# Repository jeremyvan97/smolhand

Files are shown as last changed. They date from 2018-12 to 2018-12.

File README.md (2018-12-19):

# The Smol Hand 1.0
## Introduction
The Purpose of this project is to create a decently-sized prosthetic arm, fit for a small child to use. Fit with EMG sensors, it allows the user to move the arm by twitching certain muscles, making it extremely easy to use.
This documentation goes through the design process, philosophy and schematics of the arm. For a quick look at the arm, check out this [video](https://www.youtube.com/watch?v=ZSc14HTJgZQ), which somewhat highlights the features of the arm (or at least an old version of it).

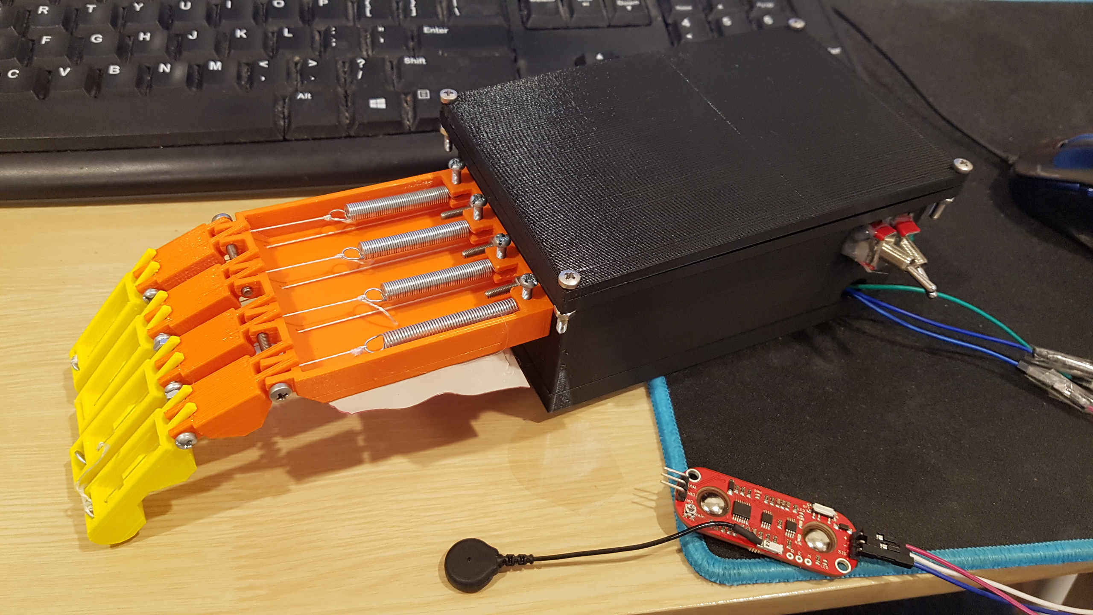
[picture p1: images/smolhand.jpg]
Smol hand


Before, we go any further, I would like to thank Yotaro Iwai, Williams Kwan and Jen Wen for being great teammates and making this a fun task.

## Disclaimer
This project was a semester-long assessment of the subject MCEN30019 Mechatronics Systems Design at the University of Melbourne. If you are currently enrolled in this subject, I **STRONGLY** advise you to design your own arm, not just because of plagiarism, but because it is more enjoyable and more knowledgeable to design one yourself (trust me).

## Let's get started

This project can be split into 3 main parts:
* Mechanical System
* Electrical System
* Software and Sensor

The gist of how the whole system works is that the sensor will read electric pulses from the user, which its readings will be then passed into a microcontroller (in this case it is an Arduino Nano). The microcontroller will then pass signals to the electrical system, which powers the actuator (a servo motor) and hence moves the mechanisms in the hand.

Throughout the project, we had decided to make the arm as simple and small as possible to accommodate for our target audience, a 10 year old child in a third world country.
>Any idiot can make something complicated. It takes good design to make something simple.
>
>-Rachel Macfarlane (quoted from somewhere else I think), 2018

## Mechanics
The mechanics behind the hand is rather simple. Each finger has two strings anchored in its top side and bottom side. The top string is connected to the palm, which is fixed. Between the palm and the string is a spring that pulls the finger back into the rest position when the servo is off.  
The bottom string is connected to the servo. When the servo is on, it pulls the finger downwards as the string creates a moment around the joints of the finger, making it curl inwards. There is a spring between the servo and the string to prevent damaging the rigid body of the arm when grabbing large objects.

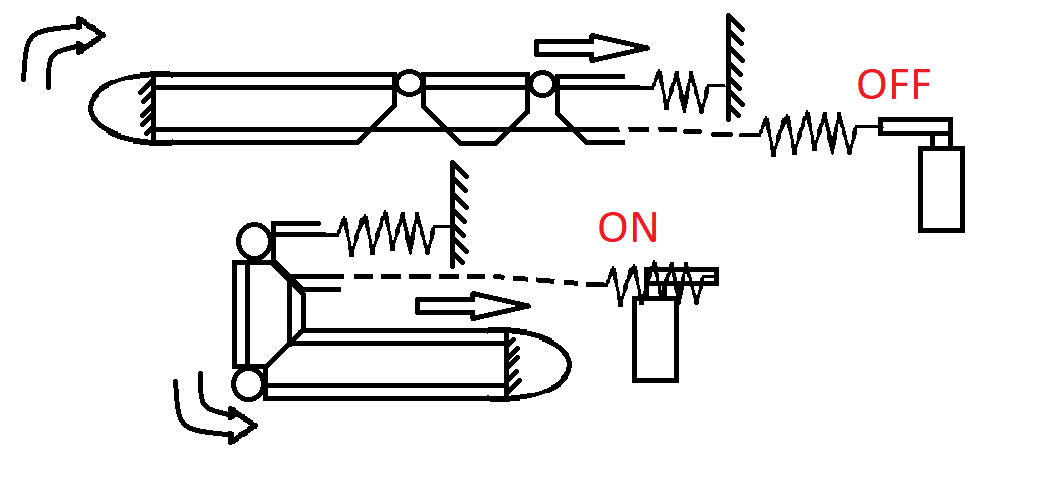
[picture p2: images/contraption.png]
Mechanics behind the fingers


We have designed these fingers to all be attached to the one same servo. This means that we **cannot** move the fingers individually. The reason we have done this is because we want to make the arm as small and light as possible for the child.

We have also decided not to give it a thumb as it might need it's own actuator, which requires more space and power. We have also found out after a bit of prototyping and experimenting that a thumb would hinder the efficiency of out design.

The parts and assembly of the arm are available in the repository for 3d printing (the .stl files must be scaled by 10x). The parts were designed in a way such that they are easy to assemble and all that is needed are M3 nuts and bolts. The finger parts have an extended end to prevent over-arching when returning to rest position. The top string goes above the bolt to create an upward moment.

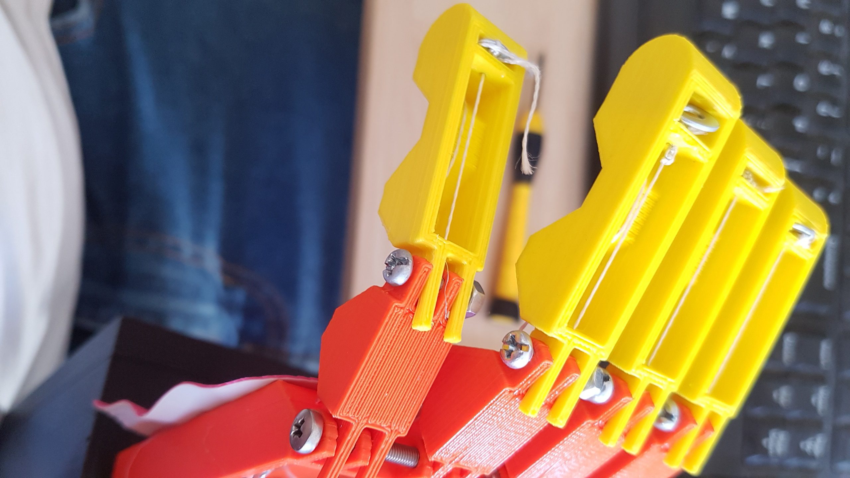
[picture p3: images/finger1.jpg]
Finger

>WD40 will always be your bestfriend.
>
>-Ethan Gan, 2018.

## Electrical
The electrical part of the arm consists of 2 switches and 2 power supplies. One of these switch-supply pairs powers the microcontroller, and the other powers the servo motor.  
A standard 9V battery is used to power the microcontroller, while the servo uses two 3.7V Li-ion batteries.

The microcontroller is connected to the EMG sensor and the servo motor. The connections for the circuit is shown below.

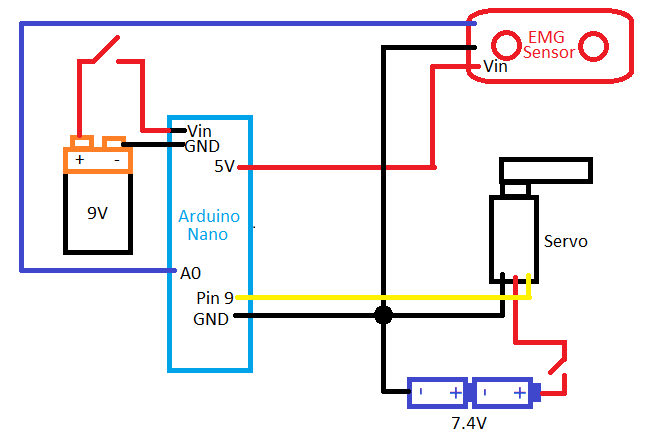
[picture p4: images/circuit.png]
Circuit


The EMG sensor reads the electrical pulses in your muscles. These readings are read by the microcontroller as a voltage depending on how strong of a pulse is given.
The microcontroller then sends a PWM signal to the servo depending on the readings read by the microcontroller.  
Here are the links to the [EMG sensors](https://www.sparkfun.com/products/13723) and [Servo motor](https://www.jaycar.com.au/servo-motor-standard-6-volt-with-metal-gear-11kg/p/YM2765) used (you could use any servo to your liking as long as you adjust the space allowed in the forearm).

A potential improvement for this circuit is to use a voltage regulator, which removes the need on a second power supply and relieving space.

## Software
The software basically makes the arm act as a finite state machine that only has 2 states: open and close. The controller only reacts when the reading is above a certain threshold (an electric pulse/muscle contraction), which then changes the state of the arm.

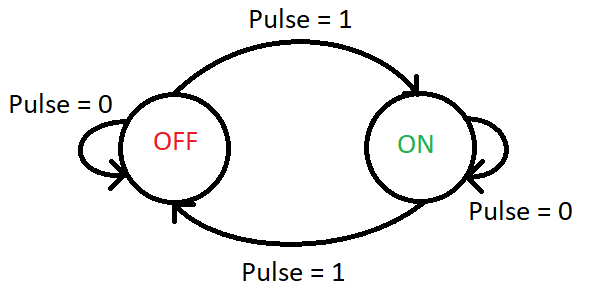
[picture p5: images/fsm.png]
Finite state machine


A possible improvement would be to implement a PID control to move the fingers at a wanted degree change instead of opening and closing entirely, though that would take a lot of time to test and calibrate.

## Assembly
The assembly should take about 2 hours. Each of the finger tips has to be connected to a joint, which is then attached to the palm.

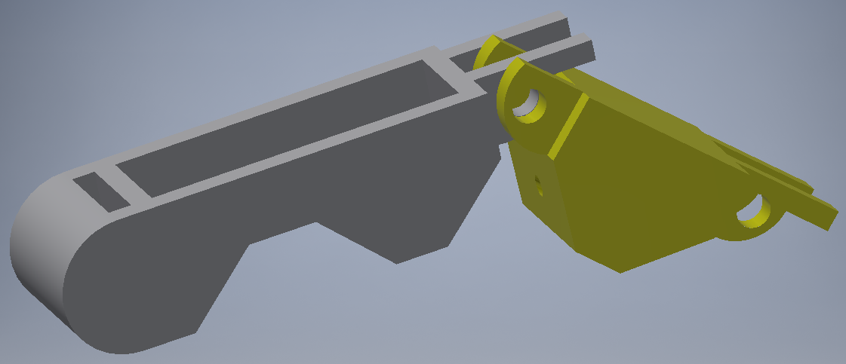
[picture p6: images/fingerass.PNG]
finger joints


Each finger should be given upper and lower strings (fishing line is what we used). Run the strings through its respective holes through the finger and the joint. Be sure that the upper string is above the bolt when assembling fingers. Once all the fingers have been assembled, run the strings into its respective holes into the palm. The palm is then attached to the forearm, which will house the electrical circuit.

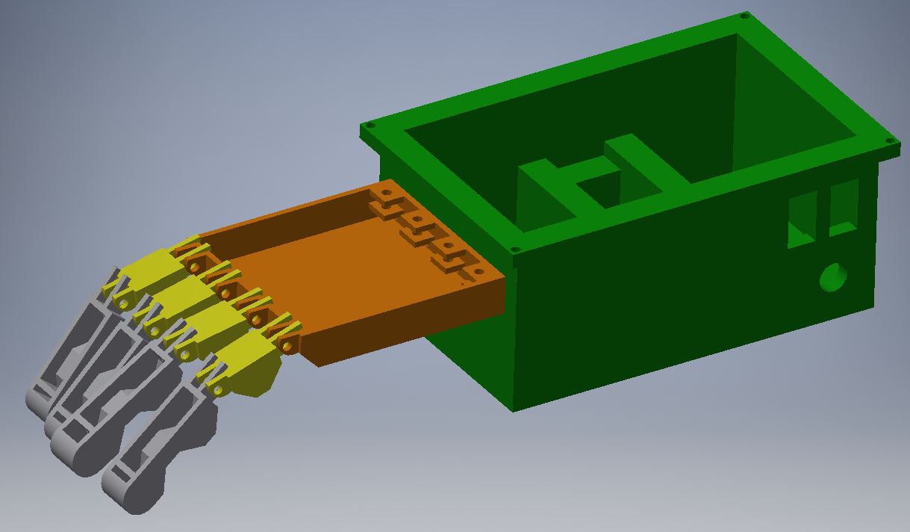
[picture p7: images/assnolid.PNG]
hand assembly


Connect the upper string to a spring each and lock them into the arm. Set up the forearm by placing the electrical components in the spaces shown below. Connect the lower strings and the servo via springs.
Sit the switches and wires through its allocated holes.

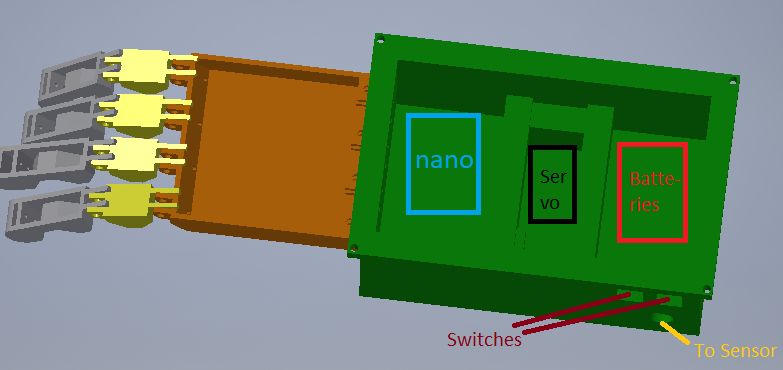
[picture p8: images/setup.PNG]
hand assembly 2


Once you have completed the assembly, it should look somewhat like this:

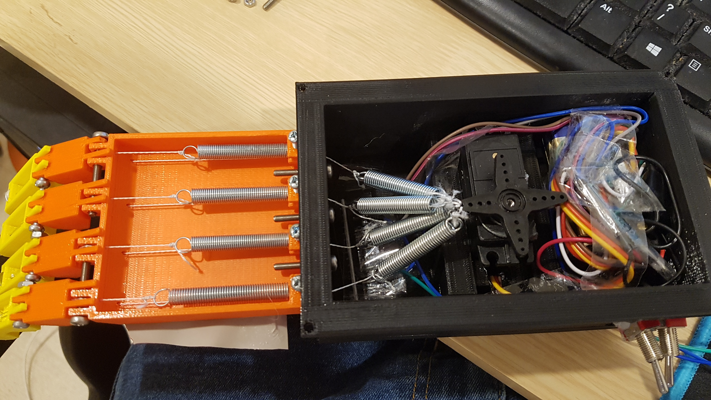
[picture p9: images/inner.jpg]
hand_irl


## Usage
Attach ECG electrodes onto the EMG sensor, then attach the electrodes to the back of your forearm (make sure the black electrode is as close to the bone as possible). Turn the switches on, and start moving your ring finger.

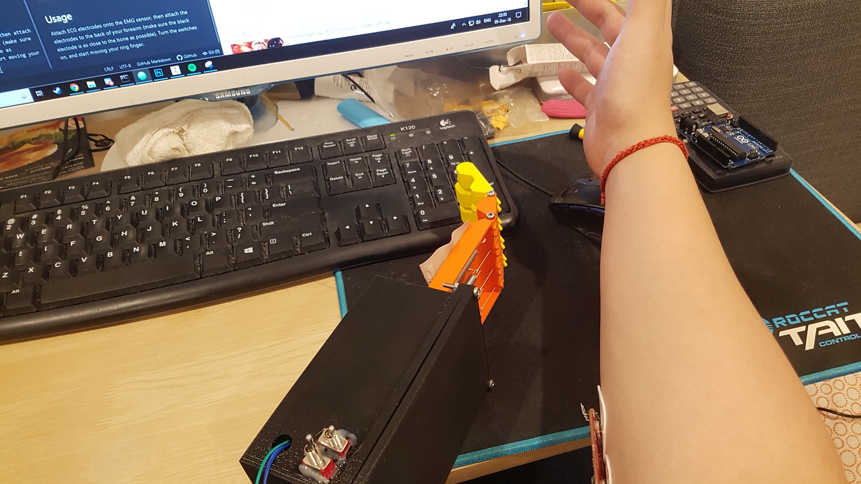
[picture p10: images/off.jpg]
off

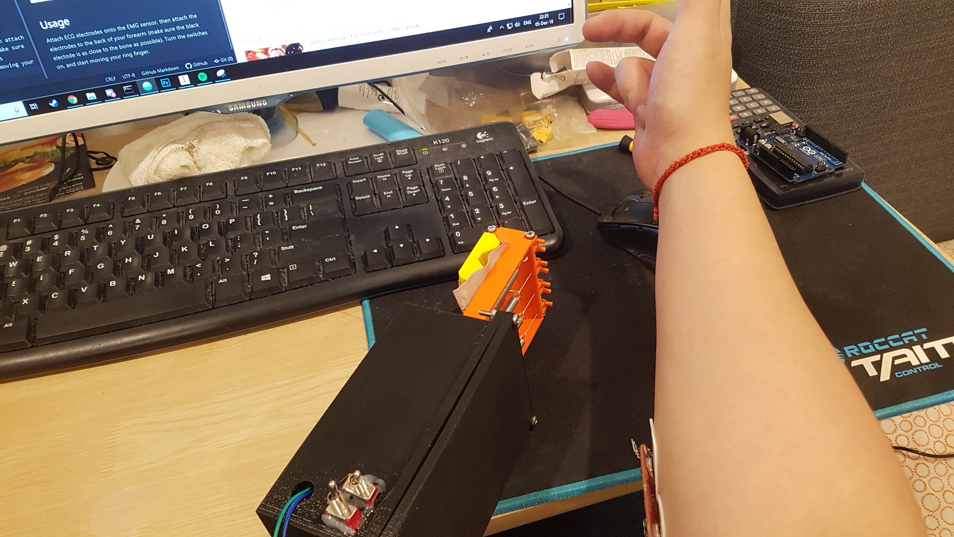
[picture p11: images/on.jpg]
on


Go ahead and start grabbing things. It makes you feel like a sort of machine, doesn't it?

Grabby

## Lessons Learnt
Throughout the project, we have learnt and understood a few concepts and philosophy behind in engineering design.
* Always think about the user. It gives you a criteria in which you will design your product around
* Complex designs aren't always better. Our design is a fairly simple yet effective one. The ability to hold many things with a tight grip and a 5.9 kg mass test shows this.
* You could achieve things that are unimaginable to people with just a few parts here and there. This project was done under $100 AUD, which is a lot less that what we have initially planned out.

## Epilogue
Anyway, there goes my 1st blog I guess. I have learnt much, from the design of the mechanical parts to the power usage of the components to how we can put everything together.

To those who are doing engineering, I wish you luck in designing and performing your projects. To those who are just starting, start thinking creatively. See improvements in everything and ask yourself: "how can I improve this?".
>Normal people... believe that if it ain't broke, don't fix it. Engineers believe that if it ain't broke, it doesn't have enough features yet.
>
>-Scott Adams

I would like to thank you for reading this. I hope you found it interesting. And to my friends and family, here's one last wacky quote.
>I hate you Alana!
>
>-John Kounetas

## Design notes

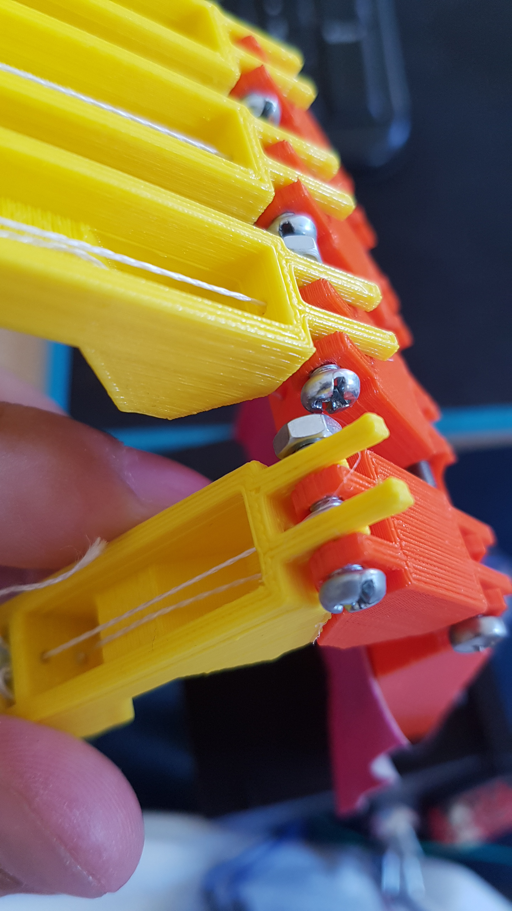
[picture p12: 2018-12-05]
images/finger2.jpg

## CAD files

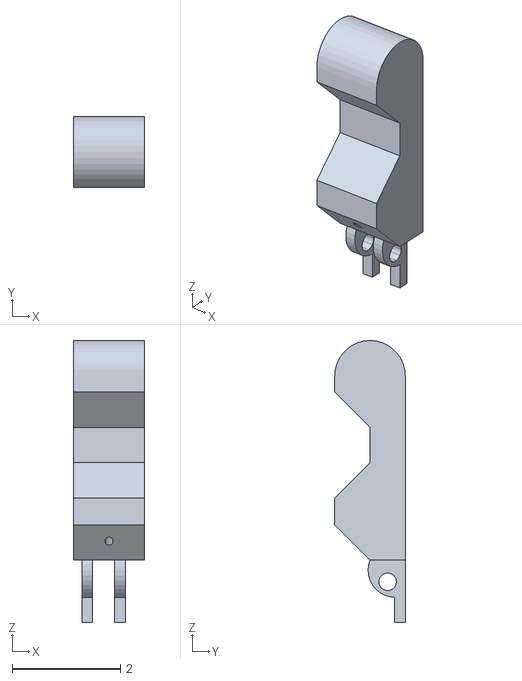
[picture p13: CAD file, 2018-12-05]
parts/pinkie.stl
1.30 x 1.30 x 5.20

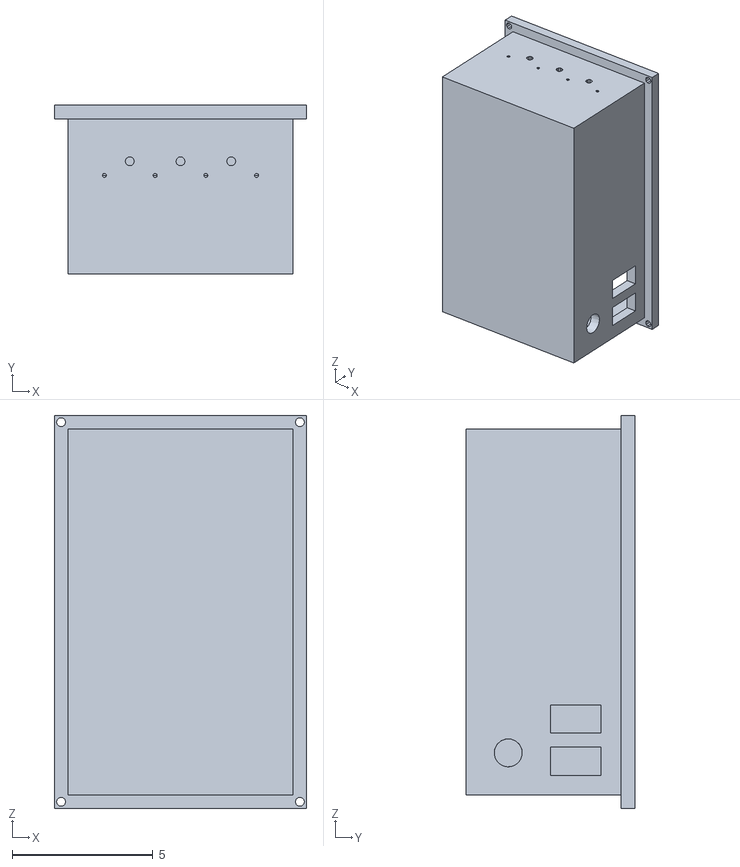
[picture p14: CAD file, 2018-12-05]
parts/mien_arm.stl
8.95 x 6.00 x 14.0

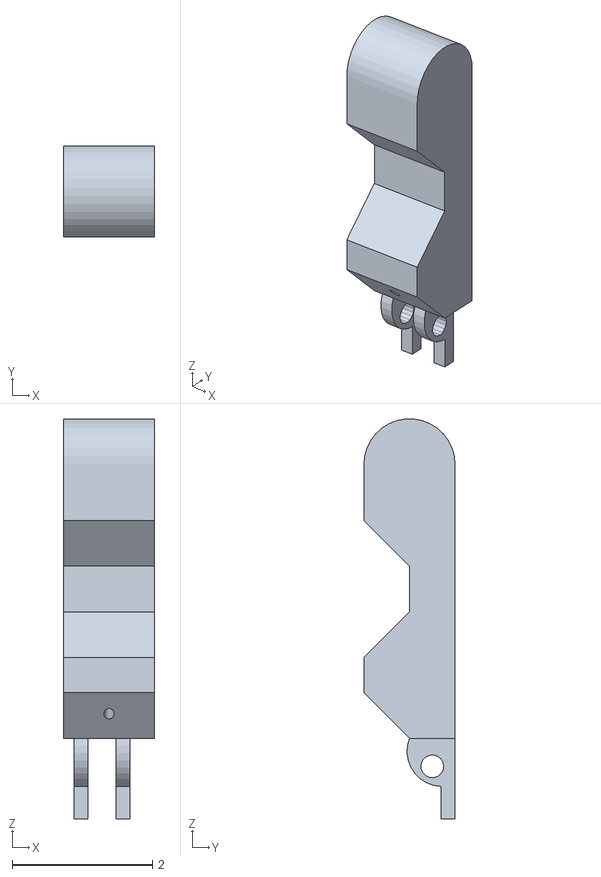
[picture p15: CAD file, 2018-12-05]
parts/middle.stl
1.30 x 1.30 x 5.70

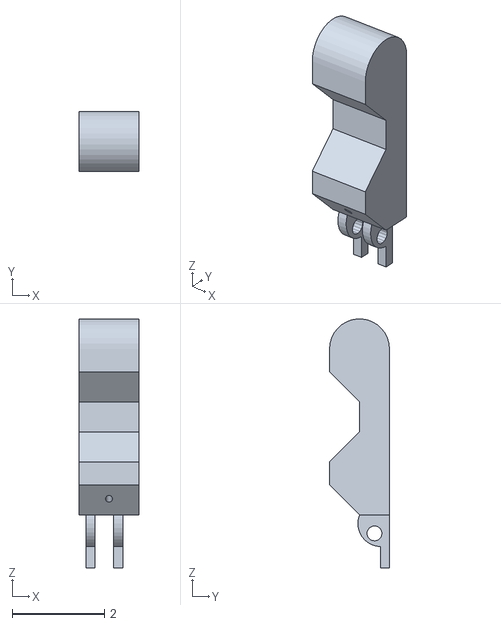
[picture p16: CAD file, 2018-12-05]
parts/index.stl
1.30 x 1.30 x 5.40

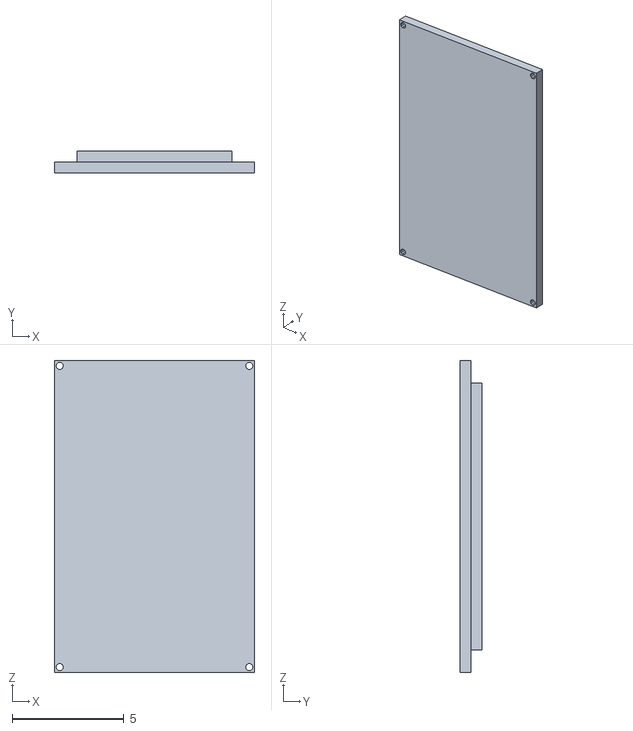
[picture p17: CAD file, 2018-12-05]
parts/mien_top.stl
8.95 x 1.00 x 13.9

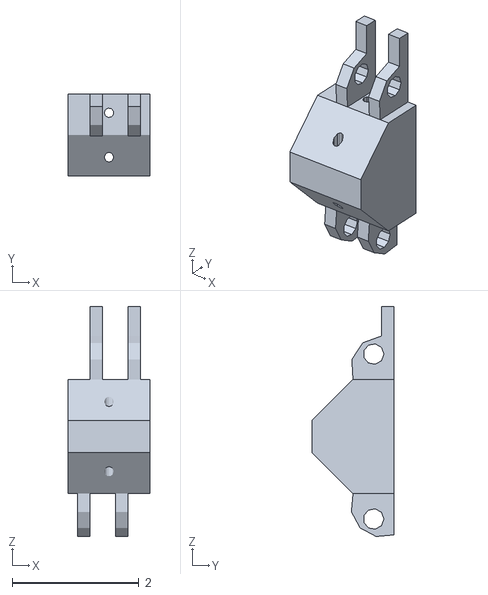
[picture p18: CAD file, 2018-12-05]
parts/finger_joins.stl
1.30 x 1.30 x 3.63

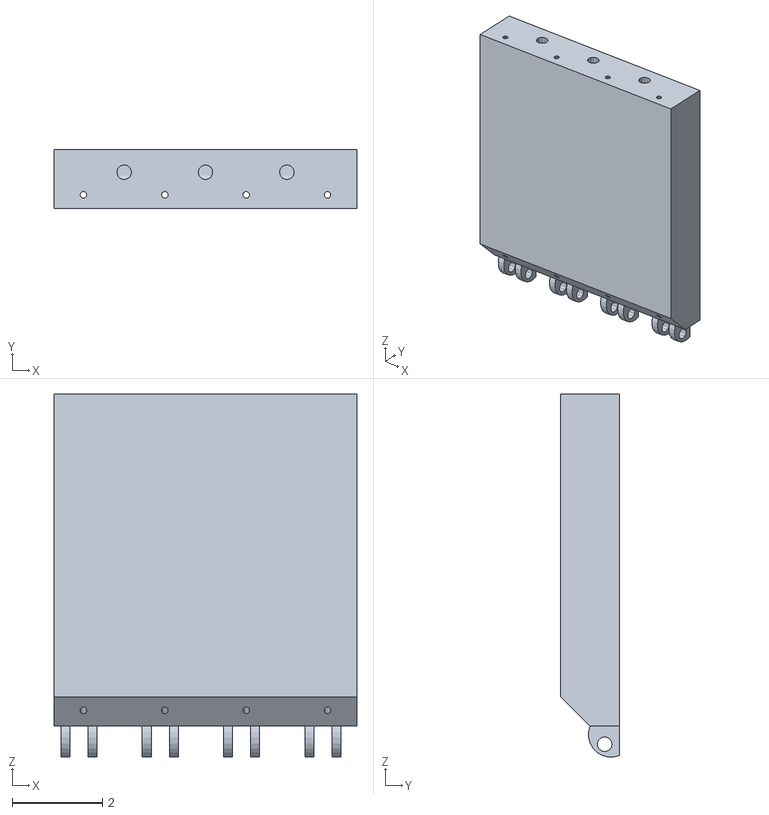
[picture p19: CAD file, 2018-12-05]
parts/palm.stl
6.70 x 1.30 x 8.03

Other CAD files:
parts/Assembly.iam
parts/finger_joins.ipt
parts/index.ipt
parts/middle.ipt
parts/mien_arm.ipt
parts/mien_top.ipt
parts/palm.ipt
parts/pinkie.ipt

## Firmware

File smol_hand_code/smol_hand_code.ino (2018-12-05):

#include <Servo.h>

// constants used
#define SENSOR A0   // reads EMG from pin A0
#define SERPIN 9    // uses pin 9 to send PWM signals to servo
#define COUNT 10    // number of counts used for moving average
#define THRESHOLD 150 // threshold of voltage reading from sensor
#define DEG 135       // degree rotation set to motor

Servo myservo;

// variables used
int rawin;
int changing = 0;

void setup() {
  // initialises sensor pin, servo and serial (for testing)
  pinMode(SENSOR, INPUT);
  myservo.attach(SERPIN);
  Serial.begin(9600);
  Serial.print(0);
  Serial.print(" ");
  Serial.print(100);  // To freeze the upper limit
  Serial.print(" ");
}

void loop() {
  
  // calculates the average of 10 readings with 10 ms intervals
  rawin = 0;
  for (int i=0; i<COUNT; i++) {
    rawin += analogRead(SENSOR);
    delay(10);
  }
  rawin = rawin / COUNT;

  Serial.println(rawin);

  // checks the state of the arm and moves it
  if (rawin >= THRESHOLD) {
    if (changing == 0) {
      swappos(myservo);
      changing = 1;
    }
  } else {
    changing = 0;
  }
  
  delay(10);
}

/** changes the state of the machine
 *  
*/
void swappos(Servo s) {
  if (s.read() == 0) {
    s.write(DEG);
  } else {
    s.write(0);
  }
}
